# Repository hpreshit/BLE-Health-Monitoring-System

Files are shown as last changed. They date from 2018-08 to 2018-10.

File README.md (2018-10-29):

# BLE based Symbiotic Health Monitoring System

This repository contains code developed for Bluetooth Low Energy client and server nodes using Silicon Labs’ Blue Gecko to set up a wireless local health monitoring network aimed for patients with heart ailments

Demo video: https://drive.google.com/file/d/1Zah0_uenn77eSVtmfuYxuPwmo54qBE38/view

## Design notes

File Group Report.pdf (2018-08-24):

## ECEN 5823

## IOT Embedded Firmware

# SYMBIOTIC HEALTH MONITORING

## Final Report

Ashish Tak
Preshit Harlikar
May 2 2018

What Problem the Project Addresses

Heart ailments remain the No. 1 global cause of death with 17.3 million deaths each year, according to “Heart Disease and Stroke Statistics”. Every year about 735,000 people have a heart attack. Of these, 525,000 are a first heart attack and 210,000 happen in people who have already had a heart attack. Apart from heart attacks, Hypoxemia is a widespread problem. Hypoxemia is a below-than-normal level of oxygen in your blood, specifically in the arteries and may have various symptoms such as shortness of breath. In this age of technology, for problems as severe as these, there needs to be a low power device capable of efficiently monitoring a person’s heart rate and blood oxygen level. If the results from the monitoring are abnormal, then the device should be capable of informing the person’s partner and/or a higher authority.

How this project alleviates or solves the problem

In this project, we consider a scenario of a couple in which both husband and wife have heart ailments. So, there would be a device for both that would monitor their heart rate and the blood oxygen saturation level after specified time intervals. If any abnormal activity is sensed on one device, then the second device will receive an alert message with the details of the parameter which is abnormal. There would also be a centralized client device, to which the heart rate and pulse oximeter data would be sent for such a scenario. Since the monitoring is done in specific time intervals and the alerts are sent only in case of abnormal activities, the system will consume less power leading to efficient monitoring.

Functional Block Diagram

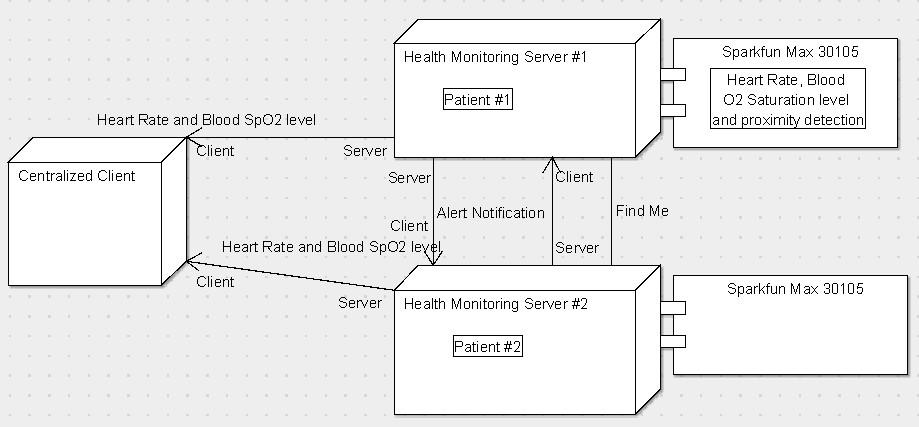
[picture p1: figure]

Summary of each individual project

Broadly, the project can be divided into two parts:
- Centralized Health Monitoring, and
- Alert notifications between peer monitoring devices

The Centralized client subscribes to the Heart Rate and Pulse Oximeter services from each of the Health Monitoring Servers via BLE. Whenever the values for either of them cross the thresholds specified for the patients, the corresponding data is reported to the centralized client. In such a scenario, the second part of the project is also activated, where it would attempt to connect to the other node via BLE and send an Alert Notification. Additionally, any of the peer nodes can use the Find Me service to activate a buzzer alarm on the other device. In the current setup, there are 2 use cases perceived for this service: to locate the other device, or to explicitly signal the partner if the person is not feeling well and an Alert Notification is not yet generated due to some sensing error.
The two parts thus help in solving the problem in a mutually exclusive fashion. The Alert Notification / Find Me services between the two peer nodes help in immediate detection of the problem, so that the partner can take the necessary first-hand corrective measures. Reporting of the abnormalities observed during the day (or week) to a centralized client device can help the physician or any other family member to keep track of the patient’s wellbeing and periodically alter their medications if required, without explicit intervention by the patients.

Verification Plan

Module | Sr. No | To be verified | Definition of Passing | Date test performed | Tested by | Measured result | Passed?
| | busy or any pending commands before performing i2c read or i2c write | In Debug mode, check the I2C Register values before sending the first Start command. Test passed if the registers have desired values | 4/2/2018 | Preshit | The registers have the desired values and no commands are pending | Passed
| 2 | Perform i2c single byte read operation from sensor | Reading a value from a specific register of the sensor, and check if the value is valid | 4/2/2018 | Ashish | The value from FIFOREADPTR register is read. | Passed
| 3 Perform single | byte write operation to the sensor | Writing a value to a register, and checking if the value is written by performing single byte read on the same register | 4/2/2018 | Preshit | Value is written to FIFOCONFIG register and read back from same register | Passed
| 4 Check if the | pulse is detected by the sensor | If the pulse is detected samples would be available in FIFODATA register of the sensor | 4/2/2018 | Ashish | New samples were available in FIFODATA register. Checked FIFOREADPTR and FIFOWRITEPTR registers and (readpointer!=writepo inter) | Passed
| 5 | Perform i2c burst read on FIFODATA register of the sensor to get the value of Red and IR LED | Desired number of bytes are read from the sensor. | 4/13/2018 | Ashish | I2C burst read performed and received the desired bytes of data. (A NACK was being sent during i2c write operation that had caused a pending NACK problem for burst read operation | Passed
I2C | 1 | Check for Bus

| | | | | which was later resolved)
6 Get a stable | Red and IR led reading from the sensor | After 60 seconds of burst read from the sensor, the readings must be stable. | 4/13/2018 | Preshit | Using letimer, a 60 second stabilizing time is used, after which the sensor readings obtained are stable. | Passed
7 | Valid Heart rate reading from sensor after processing | Heart rate reading after processing must be within range of 20-255 | 4/13/2018 | Preshit | The values are within the range of 40-145 | Passed
8 | Valid Pulse oximeter reading from sensor after processing | SpO2 value for a normal healthy person should be in range of 90% to 99%. For patients with mild respiratory diseases, the SpO2 should be 80% or above | 4/13/2018 | Preshit | The values tested were within the specified range | Passed
9 Create a Heart | rate service on the server and check if the service can be subscribed through blue gecko app and the readings are correct | The blue gecko app should be able to see the heart rate service | 4/13/2018 | Ashish | The heart rate service can be subscribed on the app and the readings are accurate. | Passed
10 Check if the | custom pulse oximeter service can be subscribed through blue gecko app and the readings are correct | The blue gecko app should be able to see the heart rate service | 4/13/2018 | Preshit | The custom pulse oximeter service can be subscribed on the app and the readings are accurate. | Passed

Particle
Sensor

BLE
Server

BLE
Client
| 11 Check if the | connection is opened between client and server | If the connection is opened, gecko_evt_le_con nection_opened_ id is triggered on the client | 4/8/2018 | Ashish | Opened Connection is displayed on LCD of the Server Gecko | Passed
| 12 Check if the | Services advertised by the server can be discovered by the client | For every service detected gecko_evt_gatt_s ervice_id event is triggered on the client | 4/8/2018 | Ashish | The services advertised by the server are displayed on the LCD of the client | Passed
| 13 Check if the | characteristics of a service can be discovered by the client | For every characteristic discovered gecko_evt_gatt_c haracteristic_id event is triggered on the client | 4/9/2018 | Ashish | The characteristics of the service are displayed on the LCD of the client | Passed
| 14 Check if a valid | characteristic value is received by the client. | For every abnormal value of heartrate or spo2 sent by the server, a notification is received through gecko_evt_gatt_c haracteristic_val ue_id event | 4/9/2018 | Ashish | A valid characteristic value is displayed on the LCD of the client. | Passed
| 15 Check if the | client can subscribe to two services simultaneousl y. | The client should subscribe to two services i.e. heartrate and pulse oximeter service for same connection. | 4/17/2018 | Ashish | The client subscribes to two services and valid readings are received | Passed
Dual-Mode Client/ Server | 16 Functional | findme service on the dual-mode client/server peer nodes | The peer node can subscribe to findme service from other peer node and the centralized | 4/27/2018 | Preshit | A peer node subscribes to the findme service from another node and the client does not. | Passed

| | | client is not triggered for this service
| 17 Functional | alert message service on dual-mode client/server peer nodes | When either heartrate or spo2 value goes above the threshold, an alert message is sent on other peer node. | 4/27/2018 | Preshit | Peer node subscribes to alert message service from other peer node for abnormal values of heartrate and spo2 | Passed
| 18 | Power off Sensor | Power off sensor by Pressing the button PB1 on either of the peer nodes | 5/1/2018 | Preshit | The sensor is put in shutdown mode when the button PB1 is pressed and turned back on if the button is pressed for the second time | Passed
| 19 Working as a | server only if the readings are above threshold | The peer nodes should function as a server only if its heartrate and spo2 readings go above threshold | 4/27/2018 | Preshit | The peer node operating as a client switches to server mode only if the readings are above threshold | Passed
MITM | 20 | Random and identical passkeys are generated on both the client and server | The passkeys generated on both the client and server are identical and random | 4/30/2018 | Ashish | The generated passkeys are displayed on the LCD and can be observed that they are random and identical | Passed
| 21 Only secured | connection is established | The client subscribes to the services from the server only when a secured connection is established | 4/30/2018 | Ashish | When the passkeys are displayed on the LCD, a button press request is offered to the user. If the user presses the button, only then is the connection established | Passed
| 22 Does not ask | for the passkey if a secured connection is | The client does not request the passkey if the bonding is established with the server. | 4/30/201 8 | Ashish | If the server has already established a secured connection with the client, the passkey request is not done and the client | Passed

| | already established | | | | subscribes to the services offered by the server
DMA | 23 | The data is logged to the desired location | The data characteristic value received by the client is logged by the DMA at given location | 4/28/2018 | Ashish | The data is logged by the DMA at given location(0x2000000) and is displayed on the LCD | Passed
| 24 | The data logged by the is the abnormal heartrate and spo2 values. | The characteristic value received by the client and the data logged by DMA should be the same | 4/28/2018 | Ashish | The data logged by the DMA are accurate i.e. the abnormal values received are being logged with any error | Passed
| 25 The threshold | values for heart rate and spo2 are stored in the persistent memory | The heart rate and spo2 threshold values can be loaded from the persistent memory | 5/1/2018 | Preshit | The values are loaded from the persistent memory and displayed on the LCD. | Passed
| 26 If no values | are loaded in the memory, the threshold values must be stored in the persistent memory | Check the persistent memory for any stored values. If no values stored, then save the threshold values on persistent memory | 5/1/2018 | Preshit | New values are stored in the persistent memory and loaded back and displayed on the LCD | Passed
Load Power Manage ment | 27 Check if the | Server always runs at lowest possible energy mode | Observe the current and average current values using Energy profiler | 5/1/2018 | Preshit | Load power management was done on the sensor by giving it a off-time of 200 ms for a period of 2 seconds. The average current was significantly reduced from 10 mA to 4.5 mA. | Passed
| 28 | Power off Sensor | Power off sensor by | 5/1/2018 | Preshit | The sensor is put in shutdown mode when | Passed

Persist
ent
Memor
y

| | Pressing the button PB1 on either of the peer nodes | | | the button PB1 is pressed and turned back on if the button is pressed for the second time. The average current in power off mode goes down to 2 mA
29 Check if the | client always runs at the lowest possible energy mode | Observe the current and average current values using Energy profiler | 5/1/2018 | Ashish | Load power management was done on the client by decreasing its scanning frequency using gecko_cmd_le_gap_set_s can_parameters(). The average current significantly dropped down to 6 mA from 10 mA | Passed

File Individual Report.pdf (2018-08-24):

## ECEN 5823

## IOT Embedded Firmware

# SYMBIOTIC HEALTH MONITORING

## Individual Report

Preshit Harlikar
May 2, 2018

What Problem the Project Addresses

Heart ailments remain the No. 1 global cause of death with 17.3 million deaths each year, according to “Heart Disease and Stroke Statistics”. Every year about 735,000 people have a heart attack. Of these, 525,000 are a first heart attack and 210,000 happen in people who have already had a heart attack. Apart from heart attacks, Hypoxemia is a widespread problem. Hypoxemia is a below-than-normal level of oxygen in your blood, specifically in the arteries and may result in various symptoms such as shortness of breath. In this age of technology, for problems as severe as these, there needs to be a low power device capable of efficiently monitoring a person’s heart rate and blood oxygen. If the results from the monitoring are abnormal, then the device should be capable of informing the person’s partner and/or a higher authority.

How this project alleviates or solves the problem

In this project, we consider a scenario of a couple in which both husband and wife have heart ailments. So, there would be a device for both that would monitor their heart rate and the blood oxygen saturation level after specified time intervals. If any abnormal activity is sensed on one device and the second device is in the proximity of the first, it will receive an alert message. There would also be a centralized client device, to which the heart rate and pulse oximeter data would be sent for such a scenario. Since the monitoring is done in specific time intervals and the alerts are sent only in case of abnormal activities, it will consume less power leading to efficient monitoring.

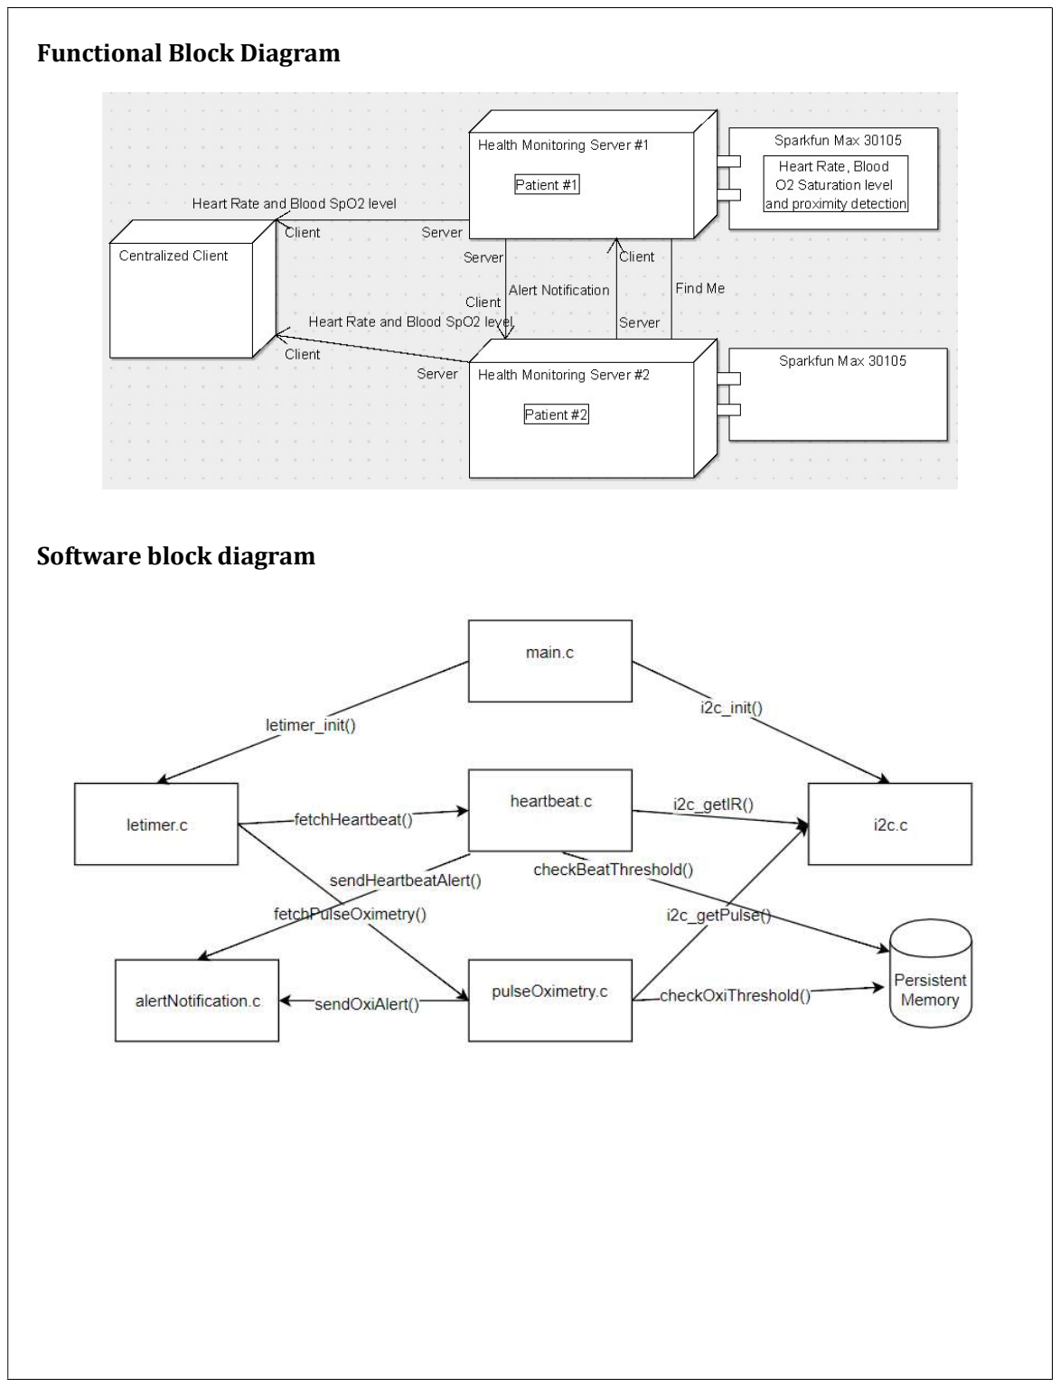
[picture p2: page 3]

Functional Block Diagram

Software block diagram

Software organization or flow chart/diagram

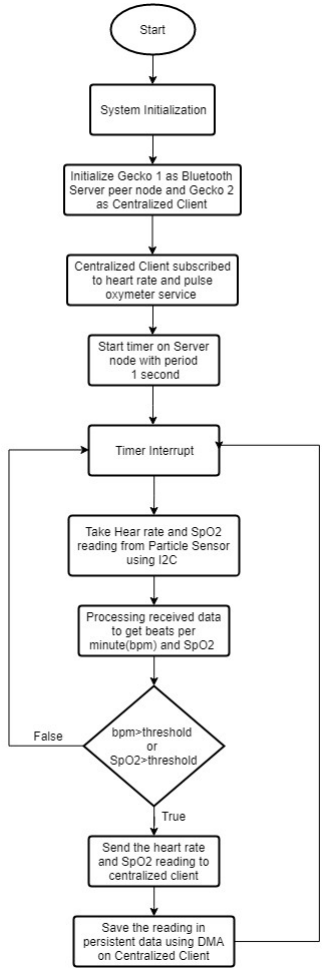
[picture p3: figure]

Development Schedule

To be completed by | Task | Team Member | Completion (as on 4/15)
04/02/2018 | Interface code to SPI LCD Display | Ashish | LCD successfully interfaced using Si Labs’ graphics library
04/02/2018 | Interface code for heart rate values via I2C. | Preshit | Heart rate reading received and processed from sensor
04/02/2018 | Interface code for pulse oximeter values via I2C. | Preshit | SpO2 reading received and processed from the sensor
04/02/2018 | Implementing use of persistent data | Ashish | The threshold values for heart rate and pulse oximetry are successfully written to persistent memory and fetched on startup
04/02/2018 | Test for sensor data by displaying values on LCD. | Ashish | The values for heart rate and pulse oximetry are observed to be stable
04/15/2018 | Setting up the four services on the servers | Ashish | The server-side code required for each service is set up successfully
04/15/2018 | Testing of services using Silicon Labs’ mobile application as a client | Preshit | The basic characteristic values for all the services are received successfully
04/15/2018 | Write code for subscribing for heart rate and pulse oximeter service on centralized client | Preshit | The client side code is set up for the centralized client to subscribe to these 2 services
04/15/2018 | Write code for subscribing for Alert Notification and Find Me service on each of the peer nodes to work as client. | Ashish | The code is set up for the nodes which will be acting as the clients to each other for these 2 particular services
04/25/2018 | Load power management during sensing and data transmission | Preshit | Load Power Management implemented on both the centralized client and individual peer nodes (details in verification plan)
04/25/2018 | Integrating DMA data transfers in application code | Ashish | DMA transfer offloaded successfully and correct values are observed on reading the memory locations

Summary of each individual project

Broadly, the project can be divided into two parts:
- Centralized Health Monitoring, and
- Alert notifications between peer monitoring devices
The Centralized client subscribes to the Heart Rate and Pulse Oximeter services from each of the Health Monitoring Servers via BLE. Whenever the values for either of them cross the thresholds specified for the patients, the corresponding data is reported to the centralized client. In such a scenario, the second part of the project is also activated, where it would attempt to connect to the other node via BLE and send an Alert Notification. Additionally, any of the peer nodes can use the Find Me service to activate a buzzer alarm on the other device. In the current setup, there are 2 use cases perceived for this service: to locate the other device, or to explicitly signal the partner if the person is not feeling well and an Alert Notification is not yet generated due to some sensing error.
The two parts thus help in solving the problem in a mutually exclusive fashion. The Alert Notification / Find Me services between the two peer nodes help in immediate detection of the problem, so that the partner can take the necessary first-hand corrective measures. Reporting of the abnormalities observed during the day (or week) to a centralized client device can help the physician or any other family member to keep track of the patient’s wellbeing and periodically alter their medications if required, without explicit intervention by the patients.

List of sensors for this project

- SparkFun Particle Sensor - MAX30105
Features:

### 1. Built-in Red, IR, and Green LEDs

2. 5V operation (3.3V is allowed, but green LED is not guaranteed to operate)

### 3. Onboard 1.8V regulation and I2C interface circuitry 4. Sensitivity configurable down to 7.81pA

5. 3200Hz maximum sample rate

### 6. Built-in 32 sample FIFO (First In, First Out)

7. Applications include presence detection, distance sensing (18" max), pulse oximetry, blood oxygen saturation level (SpO2), smoke and particle detection.

What BLE exposed services and client profiles will be implemented

For my part of this project, I will implement a centralized client device to which the server would send the heart rate and pulse oximeter data when an abnormal activity is sensed by the sensor. So, the Centralized client should be implemented that subscribes to two services: Heart rate service and Pulse oximeter service. This centralized client will be used to keep a track of the person’s abnormalities, and can be used by a physician to alter his/her medications if required, without explicit intervention by the patients.

Verification Plan

Module | Sr. No | To be verified | Definition of Passing | Date test performed | Tested by | Measured result | Passed?
| | busy or any pending commands before performing i2c read or i2c write | In Debug mode, check the I2C Register values before sending the first Start command. Test passed if the registers have desired values | 4/2/2018 | Preshit | The registers have the desired values and no commands are pending | Passed
| 2 | Perform i2c single byte read operation from sensor | Reading a value from a specific register of the sensor, and check if the value is valid | 4/2/2018 | Ashish | The value from FIFOREADPTR register is read. | Passed
| 3 Perform single | byte write operation to the sensor | Writing a value to a register, and checking if the value is written by performing single byte read on the same register | 4/2/2018 | Preshit | Value is written to FIFOCONFIG register and read back from same register | Passed
| 4 Check if the | pulse is detected by the sensor | If the pulse is detected samples would be available in FIFODATA register of the sensor | 4/2/2018 | Ashish | New samples were available in FIFODATA register. Checked FIFOREADPTR and FIFOWRITEPTR registers and (readpointer!=writepo inter) | Passed
| 5 | Perform i2c burst read on FIFODATA register of the sensor to get the value of Red and IR LED | Desired number of bytes are read from the sensor. | 4/13/2018 | Ashish | I2C burst read performed and received the desired bytes of data. (A NACK was being sent during i2c write operation that had caused a pending NACK problem for burst read operation which was later resolved) | Passed
Particle Sensor | 6 Get a stable | Red and IR led reading from the sensor | After 60 seconds of burst read from the sensor, the readings must be stable. | 4/13/2018 | Preshit | Using letimer, a 60 second stabilizing time is used, after which the sensor readings obtained are stable. | Passed
I2C | 1 | Check for Bus

7 | Valid Heart rate reading from sensor after processing | Heart rate reading after processing must be within range of 20-255 | 4/13/2018 | Preshit | The values are within the range of 40-145 | Passed
8 | Valid Pulse oximeter reading from sensor after processing | SpO2 value for a normal healthy person should be in range of 90% to 99%. For patients with mild respiratory diseases, the SpO2 should be 80% or above | 4/13/2018 | Preshit | The values tested were within the specified range | Passed
| 9 Create a Heart | rate service on the server and check if the service can be subscribed through blue gecko app and the readings are correct | The blue gecko app should be able to see the heart rate service | 4/13/2018 | Ashish | The heart rate service can be subscribed on the app and the readings are accurate. | Passed
| 10 Check if the | custom pulse oximeter service can be subscribed through blue gecko app and the readings are correct | The blue gecko app should be able to see the heart rate service | 4/13/2018 | Preshit | The custom pulse oximeter service can be subscribed on the app and the readings are accurate. | Passed
BLE Client | 11 Check if the | connection is opened between client and server | If the connection is opened, gecko_evt_le_con nection_opened_ id is triggered on the client | 4/8/2018 | Ashish | Opened Connection is displayed on LCD of the Server Gecko | Passed
| 12 Check if the | Services advertised by the server can be discovered by the client | For every service detected gecko_evt_gatt_s ervice_id event is triggered on the client | 4/8/2018 | Ashish | The services advertised by the server are displayed on the LCD of the client | Passed
| 13 Check if the | characteristics | For every characteristic | 4/9/2018 | Ashish | The characteristics of the service are | Passed

BLE
Server

| of a service can be discovered by the client | discovered gecko_evt_gatt_c haracteristic_id event is triggered on the client | | | displayed on the LCD of the client
14 Check if a valid | characteristic value is received by the client. | For every abnormal value of heartrate or spo2 sent by the server, a notification is received through gecko_evt_gatt_c haracteristic_val ue_id event | 4/9/2018 | Ashish | A valid characteristic value is displayed on the LCD of the client. | Passed
15 Check if the | client can subscribe to two services simultaneousl y. | The client should subscribe to two services i.e. heartrate and pulse oximeter service for same connection. | 4/17/2018 | Ashish | The client subscribes to two services and valid readings are received | Passed
16 Functional | findme service on the dual-mode client/server peer nodes | The peer node can subscribe to findme service from other peer node and the centralized client is not triggered for this service | 4/27/2018 | Preshit | A peer node subscribes to the findme service from another node and the client does not. | Passed
17 Functional | alert message service on dual-mode client/server peer nodes | When either heartrate or spo2 value goes above the threshold, an alert message is sent on other peer node. | 4/27/2018 | Preshit | Peer node subscribes to alert message service from other peer node for abnormal values of heartrate and spo2 | Passed
18 | Power off Sensor | Power off sensor by Pressing the button PB1 on either of the peer nodes | 5/1/2018 | Preshit | The sensor is put in shutdown mode when the button PB1 is pressed and turned back on if the button is pressed for the second time | Passed

Dual-Mode
Client/
Server

| 19 Working as a | server only if the readings are above threshold | The peer nodes should function as a server only if its heartrate and spo2 readings go above threshold | 4/27/2018 | Preshit | The peer node operating as a client switches to server mode only if the readings are above threshold | Passed
MITM | 20 | Random and identical passkeys are generated on both the client and server | The passkeys generated on both the client and server are identical and random | 4/30/2018 | Ashish | The generated passkeys are displayed on the LCD and can be observed that they are random and identical | Passed
| 21 Only secured | connection is established | The client subscribes to the services from the server only when a secured connection is established | 4/30/2018 | Ashish | When the passkeys are displayed on the LCD, a button press request is offered to the user. If the user presses the button, only then is the connection established | Passed
| 22 Does not ask | for the passkey if a secured connection is already established | The client does not request the passkey if the bonding is established with the server. | 4/30/201 8 | Ashish | If the server has already established a secured connection with the client, the passkey request is not done and the client subscribes to the services offered by the server | Passed
DMA | 23 | The data is logged to the desired location | The data characteristic value received by the client is logged by the DMA at given location | 4/28/2018 | Ashish | The data is logged by the DMA at given location(0x2000000) and is displayed on the LCD | Passed
| 24 | The data logged by the is the abnormal heartrate and spo2 values. | The characteristic value received by the client and the data logged by DMA should be the same | 4/28/2018 | Ashish | The data logged by the DMA are accurate i.e. the abnormal values received are being logged with any error | Passed
Persist ent Memor y | 25 The threshold | values for heart rate and spo2 are stored in the | The heart rate and spo2 threshold values can be loaded from the | 5/1/2018 | Preshit | The values are loaded from the persistent memory and displayed on the LCD. | Passed

| persistent memory | persistent memory
26 If no values | are loaded in the memory, the threshold values must be stored in the persistent memory | Check the persistent memory for any stored values. If no values stored, then save the threshold values on persistent memory | 5/1/2018 | Preshit | New values are stored in the persistent memory and loaded back and displayed on the LCD | Passed
27 Check if the | Server always runs at lowest possible energy mode | Observe the current and average current values using Energy profiler | 5/1/2018 | Preshit | Load power management was done on the sensor by giving it a off-time of 200 ms for a period of 2 seconds. The average current was significantly reduced from 10 mA to 4.5 mA. | Passed
28 | Power off Sensor | Power off sensor by Pressing the button PB1 on either of the peer nodes | 5/1/2018 | Preshit | The sensor is put in shutdown mode when the button PB1 is pressed and turned back on if the button is pressed for the second time. The average current in power off mode goes down to 2 mA | Passed
29 Check if the | client always runs at the lowest possible energy mode | Observe the current and average current values using Energy profiler | 5/1/2018 | Ashish | Load power management was done on the client by decreasing its scanning frequency using gecko_cmd_le_gap_set_s can_parameters(). The average current significantly dropped down to 6 mA from 10 mA | Passed

Load
Power
Manage
ment

Energy Optimization in the Project

The project has one centralized client and 2 peer nodes which operate in dual mode as either a client or a server at a instant. All 3 nodes are scan for advertising devices, and thus it was very important to implement energy optimization techniques in all of them, since scanning does indeed involve high energy usage. Scanning was optimized by setting the scanning parameters individually for the client and the peer nodes. The peer nodes, being the resource-constrained ones, scanned after an interval of 100ms with a scan window of 10ms, thus achieving a very low duty cycle of 10%. On the centralized client however, scanning was done after an interval of 100ms with a scan window of 50ms. This ensured that the centralized client did not miss any events from the servers, and moreover, since the client is a central device which would ideally be plugged in to power for the overall monitoring of both the patients, so energy optimization was not so critical for it.

Next, to implement energy optimization for the particle sensor using Load Power Management, several attempts were made to keep the sensor in a low power mode after pre-specified time intervals. However, the reliability of the readings obtained was getting severely affected by this since heart rate is such a feature which must be monitored continuously for accuracy, whenever it is.
So, energy optimization was achieved for the sensor by shutting down power to it through a GPIO pin not after pre-specified time intervals, but through a push button whenever desired by the patient. This helps in reducing the overall power consumption of the peer node, and also helps in accurate readings since whenever the readings are being fetched, they are fetched continuously without any power interruption. Further, for safety purposes, if in case the patient has not yet turned on the heart rate and pulse oximetry monitoring and he/she suddenly starts feeling uncomfortable, the system has the provision of a Find Me service to immediately send an alert to the other peer node, irrespective of the measured heart rate and pulse oximetry values.

Implementation of Man-In-The-Middle Security

The project implements Man-In-The-Middle security between the centralized client and the peer nodes, and thus protects from any corruption of data (Heart Rate and Pulse Oximetry values) being sent to the centralized client.
- To implement MITM security, identical configurations for the security requirements are initially done on both the centralized client and the peer nodes on boot-up.
- Both types of devices are set to accept new bondings.
- Next, whenever the values for heart rate or pulse oximetry cross the specified thresholds, the peer node advertises its services to the centralized client and attempts to connect to it
- Once a connection is opened, the peer node sends out a command to enhance the security of the connection
- This triggers an event on both the devices to display an identical but randomly generated passkey on the LCD
- Both the nodes need to accept this passkey using a push button, for the connection to be authenticated
- Once authenticated, the centralized client starts the service and characteristic discovery on the server node
- For subsequent connections between the same 2 set of devices, this procedure is skipped through since the connection between them is already encrypted. This is done by checking for the ‘bonding’ parameter, whenever the connection is opened between the 2 devices. Any value other than 0xFF for this parameter indicates a previous bonding handle.

Lessons learnt throughout the Project Implementation

- Dual Mode Master/Slave: Implementation of a peer node as a dual mode master/slave has been one of the biggest learning experiences while developing this project. Implementing a centralized client which subscribes to services and a server which provides characteristic values for such services was relatively straightforward. However, synchronizing the two modes in a device at once involved an in-depth understanding of the all possible states that a device can go through. A state-machine like structure was implemented to keep track of the current state and the current mode of operation of the device. Since there are some events which can be triggered for both the master and slave, it was pivotal that the state of the device be managed through such a state machine to accurately handle the incoming events. Implementing such a state machine also helps in increasing the extensibility of the project for any new kinds of services which might be required in the system.
- Interfacing the Particle Sensor for Heart Rate / Pulse Oximetry: Interfacing the MAX30105 for life-critical and high frequency services such as the Heart Rate and Pulse Oximetry was indeed a challenge. Even though a comparatively small volume of data was being sent by the sensor, yet managing the timing nuances for these services was the most important aspect. This involved adding a stabilization time after startup, fetching the readings after specified intervals and then continuously maintaining a running average. Detailed analysis and calculations from the sensor’s datasheet were required for this to interpret the digital packed values sent by the sensor.
- I2C Implementation: Working on the project actually gave novel experiences regarding the earlier known I2C protocol. The first one was regarding pending commands. It was observed that whenever any unnecessary command is transmitted to the slave via I2C, it is sent at the next available opportunity. This has the potential of corrupting the next transactions with the slave. The corruption of data for the further transactions was what led us to the second learning: of carefully analyzing the vendor’s sequence for I2C. Any command the master sends, which is not explicitly required as per the vendor specifications, does not get ignored but gets sent at the next chance, possibly damaging that transaction. The analysis for all this bit-level sequence was done using a Logic Port Analyzer, thus enhancing the hands-on exoerience with that equipment.
- DMA: Working on the add-on aspect of this project, Direct Memory Access, helped realize the importance of offloading the memory transfers to another piece of hardware. The project implemented DMA on the centralized client to move the data (abnormal heart rate and pulse oximetry values) to a specified memory location. The idea is to help a family doctor or any other family member to note the abnormalities for the patient over the day or week. Offloading the data transfer work helped achieve a consistency in the scanning intervals for the client to not miss any real-time requirements of the system.
- Managing Limited Resources: Management in a device with constrained resources was another important learning outcome through this project. The project did not implement any UART logging and simply used the on-board LCD itself for observing all kinds of data, connection details and alert messages. Since the system is designed to be a wireless and low power one, using another interface for logging purposes was not practical as per a product perspective. The system also made the best use of the 2 onboard buttons and multiplexed 4 functionalities through the 2. The state machine for the system, which was described earlier, was used to keep track of the mode to help determine which of the functionality is served by a button at a particular instant of time.

Final Status of the Individual Project:

This particular part of the project has been associated with the I2C interfacing for the sensor, and setting up the centralized client for subscribing to the heart rate and pulse oximetry. The sensor has been successfully interfaced to provide consistent values for heart rate and pulse oximetry without any breakdowns. The centralized client is also able to receive data from the servers whenever the values cross the thresholds and a substantial scanning interval is maintained on the client side to ensure that any packets are not missed. The add-on feature of DMA is also successfully implemented in the centralized client to move the incoming data values to memory through an offloading hardware. Overall, the project has reached completion with regards to the planned features.

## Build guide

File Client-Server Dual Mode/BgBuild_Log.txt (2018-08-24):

// Copyright 2018 Silicon Laboratories, Inc.
//
//

Executing: bgbuild.exe (C:\SiliconLabs\SimplicityStudio\v4\developer\sdks\gecko_sdk_suite\v2.1\protocol\bluetooth_2.7\bin\bgbuild.exe)
Standard output
ALL OK

Error/Warning output
WARNING: 2a37 length attribute is 8 but actual value length is 1. 8 will be used.
WARNING: ac05f7f0459249ea9fde003f8236d2cf max length attribute is 15 but actual value length is 1. 15 will be used.

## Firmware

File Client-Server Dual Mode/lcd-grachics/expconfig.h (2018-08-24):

/***************************************************************************//**
 * @file
 * @brief Provide EXP header configuration parameters.
 * @version 5.3.5
 *******************************************************************************
 * @section License
 * <b>Copyright 2016 Silicon Laboratories, Inc. http://www.silabs.com</b>
 *******************************************************************************
 *
 * This file is licensed under the Silicon Labs License Agreement. See the file
 * "Silabs_License_Agreement.txt" for details. Before using this software for
 * any purpose, you must agree to the terms of that agreement.
 *
 ******************************************************************************/

#ifndef EXPCONFIG_H
#define EXPCONFIG_H

#define BSP_EXP_HEADER3_PIN    2
#define BSP_EXP_HEADER3_PORT   gpioPortA
#define BSP_EXP_HEADER4_PIN    6
#define BSP_EXP_HEADER4_PORT   gpioPortC
#define BSP_EXP_HEADER5_PIN    3
#define BSP_EXP_HEADER5_PORT   gpioPortA
#define BSP_EXP_HEADER6_PIN    7
#define BSP_EXP_HEADER6_PORT   gpioPortC
#define BSP_EXP_HEADER7_PIN    6
#define BSP_EXP_HEADER7_PORT   gpioPortF
#define BSP_EXP_HEADER8_PIN    8
#define BSP_EXP_HEADER8_PORT   gpioPortC
#define BSP_EXP_HEADER9_PIN    7
#define BSP_EXP_HEADER9_PORT   gpioPortF
#define BSP_EXP_HEADER10_PIN   9
#define BSP_EXP_HEADER10_PORT  gpioPortC
#define BSP_EXP_HEADER11_PIN   4
#define BSP_EXP_HEADER11_PORT  gpioPortF
#define BSP_EXP_HEADER12_PIN   0
#define BSP_EXP_HEADER12_PORT  gpioPortA
#define BSP_EXP_HEADER13_PIN   3
#define BSP_EXP_HEADER13_PORT  gpioPortF
#define BSP_EXP_HEADER14_PIN   1
#define BSP_EXP_HEADER14_PORT  gpioPortA
#define BSP_EXP_HEADER15_PIN   10
#define BSP_EXP_HEADER15_PORT  gpioPortC
#define BSP_EXP_HEADER16_PIN   11
#define BSP_EXP_HEADER16_PORT  gpioPortC

#define BSP_EXP_I2C            I2C0
#define BSP_EXP_I2C_SCL_LOC    _I2C_ROUTELOC0_SCLLOC_LOC14
#define BSP_EXP_I2C_SCL_PIN    BSP_EXP_HEADER15_PIN
#define BSP_EXP_I2C_SCL_PORT   BSP_EXP_HEADER15_PORT
#define BSP_EXP_I2C_SDA_LOC    _I2C_ROUTELOC0_SDALOC_LOC16
#define BSP_EXP_I2C_SDA_PIN    BSP_EXP_HEADER16_PIN
#define BSP_EXP_I2C_SDA_PORT   BSP_EXP_HEADER16_PORT

#define BSP_EXP_SPI            USART1
#define BSP_EXP_SPI_CLK_LOC    _USART_ROUTELOC0_CLKLOC_LOC11
#define BSP_EXP_SPI_CLK_PIN    BSP_EXP_HEADER8_PIN
#define BSP_EXP_SPI_CLK_PORT   BSP_EXP_HEADER8_PORT
#define BSP_EXP_SPI_CS_LOC     _USART_ROUTELOC0_CSLOC_LOC11
#define BSP_EXP_SPI_CS_PIN     BSP_EXP_HEADER10_PIN
#define BSP_EXP_SPI_CS_PORT    BSP_EXP_HEADER10_PORT
#define BSP_EXP_SPI_MISO_LOC   _USART_ROUTELOC0_RXLOC_LOC11
#define BSP_EXP_SPI_MISO_PIN   BSP_EXP_HEADER6_PIN
#define BSP_EXP_SPI_MISO_PORT  BSP_EXP_HEADER6_PORT
#define BSP_EXP_SPI_MOSI_LOC   _USART_ROUTELOC0_TXLOC_LOC11
#define BSP_EXP_SPI_MOSI_PIN   BSP_EXP_HEADER4_PIN
#define BSP_EXP_SPI_MOSI_PORT  BSP_EXP_HEADER4_PORT

#define BSP_EXP_USART          USART0
#define BSP_EXP_USART_CTS_LOC  _USART_ROUTELOC1_CTSLOC_LOC30
#define BSP_EXP_USART_CTS_PIN  BSP_EXP_HEADER3_PIN
#define BSP_EXP_USART_CTS_PORT BSP_EXP_HEADER3_PORT
#define BSP_EXP_USART_RTS_LOC  _USART_ROUTELOC1_RTSLOC_LOC30
#define BSP_EXP_USART_RTS_PIN  BSP_EXP_HEADER5_PIN
#define BSP_EXP_USART_RTS_PORT BSP_EXP_HEADER5_PORT
#define BSP_EXP_USART_RX_LOC   _USART_ROUTELOC0_RXLOC_LOC0
#define BSP_EXP_USART_RX_PIN   BSP_EXP_HEADER14_PIN
#define BSP_EXP_USART_RX_PORT  BSP_EXP_HEADER14_PORT
#define BSP_EXP_USART_TX_LOC   _USART_ROUTELOC0_TXLOC_LOC0
#define BSP_EXP_USART_TX_PIN   BSP_EXP_HEADER12_PIN
#define BSP_EXP_USART_TX_PORT  BSP_EXP_HEADER12_PORT

#endif /* EXPCONFIG_H */

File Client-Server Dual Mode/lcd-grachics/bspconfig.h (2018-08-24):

/***************************************************************************//**
 * @file
 * @brief Provide BSP (board support package) configuration parameters.
 * @version 5.3.5
 *******************************************************************************
 * # License
 * <b>Copyright 2015 Silicon Labs, Inc. http://www.silabs.com</b>
 *******************************************************************************
 *
 * This file is licensed under the Silabs License Agreement. See the file
 * "Silabs_License_Agreement.txt" for details. Before using this software for
 * any purpose, you must agree to the terms of that agreement.
 *
 ******************************************************************************/

#ifndef __SILICON_LABS_BSPCONFIG_H
#define __SILICON_LABS_BSPCONFIG_H

#define BSP_STK
#define BSP_WSTK
#define BSP_WSTK6102A_BGM121

#define BSP_BCC_USART         USART0
#define BSP_BCC_CLK           cmuClock_USART0
#define BSP_BCC_TX_LOCATION   USART_ROUTELOC0_TXLOC_LOC0
#define BSP_BCC_RX_LOCATION   USART_ROUTELOC0_RXLOC_LOC0
#define BSP_BCC_TXPORT        gpioPortA
#define BSP_BCC_TXPIN         0
#define BSP_BCC_RXPORT        gpioPortA
#define BSP_BCC_RXPIN         1
#define BSP_BCC_ENABLE_PORT   gpioPortA
#define BSP_BCC_ENABLE_PIN    5                 /* VCOM_ENABLE */

#define BSP_DISP_ENABLE_PORT  gpioPortD
#define BSP_DISP_ENABLE_PIN   15                /* MemLCD display enable */

#define BSP_EXTFLASH_PRESENT 1

#define BSP_GPIO_LEDS
#define BSP_NO_OF_LEDS          2
#define BSP_GPIO_LED0_PORT      gpioPortF
#define BSP_GPIO_LED0_PIN       4
#define BSP_GPIO_LED1_PORT      gpioPortF
#define BSP_GPIO_LED1_PIN       5
#define BSP_GPIO_LEDARRAY_INIT { { BSP_GPIO_LED0_PORT, BSP_GPIO_LED0_PIN }, { BSP_GPIO_LED1_PORT, BSP_GPIO_LED1_PIN } }

#define BSP_GPIO_BUTTONS
#define BSP_NO_OF_BUTTONS       2
#define BSP_GPIO_PB0_PORT       gpioPortF
#define BSP_GPIO_PB0_PIN        6
#define BSP_GPIO_PB1_PORT       gpioPortF
#define BSP_GPIO_PB1_PIN        7

#define BSP_GPIO_BUTTONARRAY_INIT { { BSP_GPIO_PB0_PORT, BSP_GPIO_PB0_PIN }, { BSP_GPIO_PB1_PORT, BSP_GPIO_PB1_PIN } }

#define BSP_INIT_DEFAULT  0

#if !defined(EMU_DCDCINIT_WSTK_DEFAULT)
/* Use emlib defaults */
#define EMU_DCDCINIT_WSTK_DEFAULT       EMU_DCDCINIT_DEFAULT
#endif

#if !defined(CMU_HFXOINIT_WSTK_DEFAULT)
#define CMU_HFXOINIT_WSTK_DEFAULT                                          \
  {                                                                        \
    false,      /* Low-noise mode for EFR32 */                             \
    false,      /* Disable auto-start on EM0/1 entry */                    \
    false,      /* Disable auto-select on EM0/1 entry */                   \
    false,      /* Disable auto-start and select on RAC wakeup */          \
    _CMU_HFXOSTARTUPCTRL_CTUNE_DEFAULT,                                    \
    0x142,      /* Steady-state CTUNE for WSTK boards without load caps */ \
    _CMU_HFXOSTEADYSTATECTRL_REGISH_DEFAULT,                               \
    0x20,       /* Matching errata fix in CHIP_Init() */                   \
    0x7,        /* Recommended steady-state osc core bias current */       \
    0x6,        /* Recommended peak detection threshold */                 \
    _CMU_HFXOTIMEOUTCTRL_SHUNTOPTTIMEOUT_DEFAULT,                          \
    0xA,        /* Recommended peak detection timeout  */                  \
    0x4,        /* Recommended steady timeout */                           \
    _CMU_HFXOTIMEOUTCTRL_STARTUPTIMEOUT_DEFAULT,                           \
    cmuOscMode_Crystal,                                                    \
  }
#endif

#if !defined(RADIO_PTI_INIT)
#define RADIO_PTI_INIT                                                     \
  {                                                                        \
    RADIO_PTI_MODE_UART,    /* Simplest output mode is UART mode */        \
    1600000,                /* Choose 1.6 MHz for best compatibility */    \
    6,                      /* WSTK uses location 6 for DOUT */            \
    gpioPortB,              /* Get the port for this loc */                \
    12,                     /* Get the pin, location should match above */ \
    6,                      /* WSTK uses location 6 for DCLK */            \
    gpioPortB,              /* Get the port for this loc */                \
    11,                     /* Get the pin, location should match above */ \
    6,                      /* WSTK uses location 6 for DFRAME */          \
    gpioPortB,              /* Get the port for this loc */                \
    13,                     /* Get the pin, location should match above */ \
  }
#endif

#if !defined(RAIL_PTI_CONFIG)
#define RAIL_PTI_CONFIG                                                    \
  {                                                                        \
    RAIL_PTI_MODE_UART,     /* Simplest output mode is UART mode */        \
    1600000,                /* Choose 1.6 MHz for best compatibility */    \
    6,                      /* WSTK uses location 6 for DOUT */            \
    gpioPortB,              /* Get the port for this loc */                \
    12,                     /* Get the pin, location should match above */ \
    6,                      /* WSTK uses location 6 for DCLK */            \
    gpioPortB,              /* Get the port for this loc */                \
    11,                     /* Get the pin, location should match above */ \
    6,                      /* WSTK uses location 6 for DFRAME */          \
    gpioPortB,              /* Get the port for this loc */                \
    13,                     /* Get the pin, location should match above */ \
  }
#endif

#if !defined(RADIO_PA_2P4_INIT)
#define RADIO_PA_2P4_INIT                                    \
  {                                                          \
    PA_SEL_2P4_HP,    /* Power Amplifier mode */             \
    PA_VOLTMODE_DCDC, /* Power Amplifier vPA Voltage mode */ \
    100,              /* Desired output power in dBm * 10 */ \
    0,                /* Output power offset in dBm * 10 */  \
    10,               /* Desired ramp time in us */          \
  }
#endif

#if !defined(RAIL_PA_2P4_CONFIG)
#define RAIL_PA_2P4_CONFIG                                            \
  {                                                                   \
    RAIL_TX_POWER_MODE_2P4_HP, /* Power Amplifier mode */             \
    1800,                      /* Power Amplifier vPA Voltage mode */ \
    10,                        /* Desired ramp time in us */          \
  }
#endif

#if !defined(RADIO_PA_SUBGIG_INIT)
#define RADIO_PA_SUBGIG_INIT                                 \
  {                                                          \
    PA_SEL_SUBGIG,    /* Power Amplifier mode */             \
    PA_VOLTMODE_DCDC, /* Power Amplifier vPA Voltage mode */ \
    100,              /* Desired output power in dBm * 10 */ \
    0,                /* Output power offset in dBm * 10 */  \
    10,               /* Desired ramp time in us */          \
  }
#endif

#if !defined(RAIL_PA_SUBGIG_CONFIG)
#define RAIL_PA_SUBGIG_CONFIG                                         \
  {                                                                   \
    RAIL_TX_POWER_MODE_SUBGIG, /* Power Amplifier mode */             \
    1800,                      /* Power Amplifier vPA Voltage mode */ \
    10,                        /* Desired ramp time in us */          \
  }
#endif

#if !defined(RAIL_PA_DEFAULT_POWER)
#define RAIL_PA_DEFAULT_POWER 100
#endif

#define BSP_BCP_VERSION 2
#include "bsp_bcp.h"

#endif /* __SILICON_LABS_BSPCONFIG_H */

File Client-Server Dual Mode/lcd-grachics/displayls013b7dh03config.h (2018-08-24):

/**************************************************************************//**
* @file displayls013b7dh03config.h
* @brief BRD4302A specific configuration for the display driver for
*        the Sharp Memory LCD model LS013B7DH03.
* @version 5.3.5
******************************************************************************
* # License

* <b>Copyright 2015 Silicon Labs, Inc. http://www.silabs.com</b>
*******************************************************************************
*
* This file is licensed under the Silabs License Agreement. See the file
* "Silabs_License_Agreement.txt" for details. Before using this software for
* any purpose, you must agree to the terms of that agreement.
*
******************************************************************************/

#ifndef __SILICON_LABS_DISPLAY_LS013B7DH03_CONFIG_H_
#define __SILICON_LABS_DISPLAY_LS013B7DH03_CONFIG_H_

#include "displayconfigapp.h"

/* Display device name. */
#define SHARP_MEMLCD_DEVICE_NAME   "Sharp LS013B7DH03 #1"

/* LCD and SPI GPIO pin connections on the EFR32BG1_BRD4302A. */
#define LCD_PORT_SCLK           (gpioPortC)
#define LCD_PIN_SCLK            (6)
#define LCD_PORT_SI             (gpioPortC)
#define LCD_PIN_SI              (7)
#define LCD_PORT_SCS            (gpioPortD)
#define LCD_PIN_SCS             (14)
#define LCD_PORT_EXTCOMIN       (gpioPortD)
#define LCD_PIN_EXTCOMIN        (13)
#define LCD_PORT_DISP_SEL       (gpioPortD)
#define LCD_PIN_DISP_SEL        (15)
#define LCD_PORT_DISP_PWR       (gpioPortD)
#define LCD_PIN_DISP_PWR        (15)

/* PRS settings for polarity inversion extcomin auto toggle.  */
#define LCD_AUTO_TOGGLE_PRS_CH    (4)  /* PRS channel 4.      */
#define LCD_AUTO_TOGGLE_PRS_ROUTELOC()  PRS->ROUTELOC1 = \
  ((PRS->ROUTELOC1 & ~_PRS_ROUTELOC1_CH4LOC_MASK) | PRS_ROUTELOC1_CH4LOC_LOC4)
#define LCD_AUTO_TOGGLE_PRS_ROUTEPEN    PRS_ROUTEPEN_CH4PEN

/*
 * Select how LCD polarity inversion should be handled:
 *
 * If POLARITY_INVERSION_EXTCOMIN is defined,
 * the polarity inversion is armed for every rising edge of the EXTCOMIN
 * pin. The actual polarity inversion is triggered at the next transision of
 * SCS. This mode is recommended because it causes less CPU and SPI load than
 * the alternative mode, see below.
 * If POLARITY_INVERSION_EXTCOMIN is undefined,
 * the polarity inversion is toggled by sending an SPI command. This mode
 * causes more CPU and SPI load than using the EXTCOMIN pin mode.
 */
#define POLARITY_INVERSION_EXTCOMIN

/* Define POLARITY_INVERSION_EXTCOMIN_PAL_AUTO_TOGGLE if you want the PAL
 * (Platform Abstraction Layer interface) to automatically toggle the EXTCOMIN
 *  pin.
 * If the PAL_TIMER_REPEAT function is defined the EXTCOMIN toggling is handled
 * by a timer repeat system, therefore we must undefine
 * POLARITY_INVERSION_EXTCOMIN_PAL_AUTO_TOGGLE;
 */
#ifndef PAL_TIMER_REPEAT_FUNCTION
  #define POLARITY_INVERSION_EXTCOMIN_PAL_AUTO_TOGGLE
#endif
#endif /* __SILICON_LABS_DISPLAY_LS013B7DH03_CONFIG_H_ */
